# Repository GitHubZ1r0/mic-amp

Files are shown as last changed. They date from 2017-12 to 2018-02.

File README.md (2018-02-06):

# Microphone amplifier for Knowles Electret microphones

## Overview
This printed circuit board (PCB) is based on the design created at Eaton
Peabody Laboratories (Mass. Eye and Ear Infirmary), but redesigned to work at
lower frequencies. It features:

* High-pass input filter with 96 Hz cutoff.
* Selectable 20 or 40 dB gain
* Low-pass amplification with a 72 kHz cutoff.
* Low-noise 1.5V supply for microphone with a low-pass filter cutoff of 0.33 Hz
  (ensuring that very little noise makes it into the microphone).

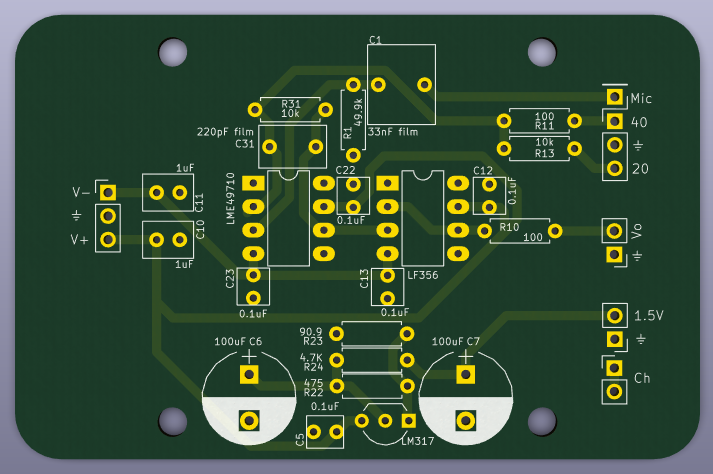
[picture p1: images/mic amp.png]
Rendering of PCB


The board is 74mm x 48mm and the mounting holes, spaced 40mm x 40mm, are sized
for a M3 screw. The board will fit in a Hammond enclosure that accomodates 75mm
wide boards.

## Getting started
OSH Park will print and ship three of these boards for approximately $30. 

Order the parts from the [bill of materials](part%20list.md).

Solder the parts using solder with water-soluble flux.

Wash the board with dH<sub>2</sub>O.

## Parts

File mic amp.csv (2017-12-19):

Reference | Quantity | Value | Footprint | Datasheet
C1 | 1 | 33nF film | Capacitor_THT:C_Rect_L7.2mm_W8.5mm_P5.00mm_FKP2_FKP2_MKS2_MKP2
C10 C11 | 2 | 1uF | custom:C_Rect_L5.5mm_W3.15mm_P2.50mm
C12 C13 C22 C23 | 4 | 0.1uF | custom:C_Rect_L4.5mm_W3.15mm_P2.50mm
C31 | 1 | 220pF film | Capacitor_THT:C_Rect_L7.2mm_W4.5mm_P5.00mm_FKS2_FKP2_MKS2_MKP2
C5 | 1 | 0.1uF | custom:C_Rect_L5.5mm_W3.15mm_P2.50mm
C6 C7 | 2 | 100uF | Capacitor_THT:CP_Radial_D10.0mm_P5.00mm
J2 | 1 | CONN_01X01 | Conn_PinSocket_2.54mm:PinSocket_1x01_P2.54mm_Vertical
J3 | 1 | CONN_01X03 | Conn_PinSocket_2.54mm:PinSocket_1x03_P2.54mm_Vertical
J4 J5 J6 J7 | 4 | CONN_01X01 | MountingHole:MountingHole_3.2mm_M3
J1 J8 | 2 | CONN_01X02 | Conn_PinSocket_2.54mm:PinSocket_1x02_P2.54mm_Vertical
J9 | 1 | CONN_01X05 | Conn_PinSocket_2.54mm:PinSocket_1x05_P2.54mm_Vertical
R1 | 1 | 49.9k | Resistor_THT:R_Axial_DIN0207_L6.3mm_D2.5mm_P7.62mm_Horizontal
R10 R11 | 2 | 100 | Resistor_THT:R_Axial_DIN0207_L6.3mm_D2.5mm_P7.62mm_Horizontal
R13 R31 | 2 | 10k | Resistor_THT:R_Axial_DIN0207_L6.3mm_D2.5mm_P7.62mm_Horizontal
R22 | 1 | 475 | Resistor_THT:R_Axial_DIN0207_L6.3mm_D2.5mm_P7.62mm_Horizontal
R23 | 1 | 90.9 | Resistor_THT:R_Axial_DIN0207_L6.3mm_D2.5mm_P7.62mm_Horizontal
R24 | 1 | 4.7K | Resistor_THT:R_Axial_DIN0207_L6.3mm_D2.5mm_P7.62mm_Horizontal
U1 | 1 | LME49710 | Package_DIP:DIP-8_W7.62mm_LongPads
U2 | 1 | LF356 | Package_DIP:DIP-8_W7.62mm_LongPads
VREG1 | 1 | LM317 | Package_TO_SOT_THT:TO-92_Inline_Wide

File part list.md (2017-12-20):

| References             | Number | Value      | Part number        | Note                                                   |
| ---------------------- | ------ | ---------- | ------------------ | ------------------------------------------------------ |
| C1                     | 1      | 33nF       | FKP2C023301L00HI00 | use metal film                                         |
| C5, C12, C13, C22, C23 | 5      | 0.1uF      | RDER72A104K1S1H03A |                                                        |
| C6, C7                 | 2      | 100uF      | UKL1V101KPDANA     |                                                        |
| C10, C11               | 2      | 1uF        | RDER72A105K2P1H03B |                                                        |
| C31                    | 1      | 220pF      | FKP2D002201D00HSSD | use metal film                                         |
| J1, J8, J10            | 3      | CONN_01X02 |                    | 0.1" header                                            |
| J2                     | 1      | CONN_01X01 |                    | 0.1" header                                            |
| J3, J9                 | 2      | CONN_01X03 |                    | 0.1" header                                            |
| J4, J5, J6, J7         | 4      | CONN_01X01 |                    | mounting hole                                          |
| R1                     | 1      | 49.9k      | YR1B49K9CC         |                                                        |
| R10, R11               | 2      | 100        | YR1B100RCC         |                                                        |
| R13                    | 1      | 1k         | YR1B1K0CC          |                                                        |
| R22                    | 1      | 475        | YR1B499RCC         |                                                        |
| R23                    | 1      | 90.9       | YR1B90R9CC         |                                                        |
| R24                    | 1      | 4.7K       | YR1B4K75CC         |                                                        |
| R31                    | 1      | 10k        | YR1B10KCC          |                                                        |
| U1                     | 1      | LME49710   | LME49710NA/NOPB    | this part is end-of-life, order extra if you need more |
| U2                     | 1      | LF356      | LF356N/NOPB        |                                                        |
| VREG1                  | 1      | LM317      | LM317LZ/NOPB       |                                                        |

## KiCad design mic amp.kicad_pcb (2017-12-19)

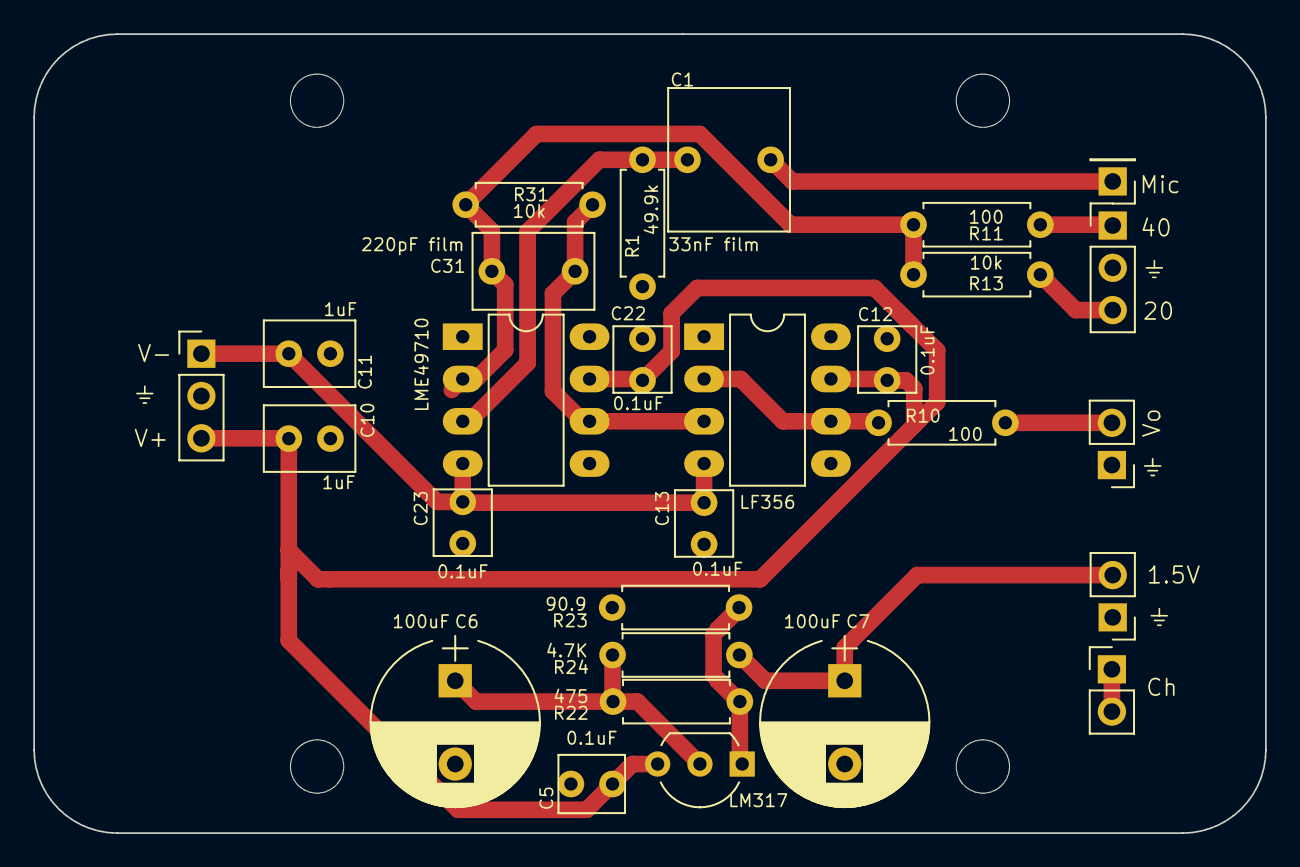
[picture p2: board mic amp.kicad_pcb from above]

Board: 2 copper layers, 74.0 x 48.0 mm, 32 parts (0 on the bottom side), 15 nets.

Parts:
C1: 33nF film; C_Rect_L7.2mm_W8.5mm_P5.00mm_FKP2_FKP2_MKS2_MKP2
C5, C12, C13, C22, C23: 0.1uF; C_Rect_L4.0mm_W3.5mm_P2.50mm
C6, C7: 100uF; CP_Radial_D10.0mm_P5.00mm
C10, C11: 1uF; C_Rect_L5.5mm_W4.0mm_P2.50mm
C31: 220pF film; C_Rect_L7.2mm_W4.5mm_P5.00mm_FKS2_FKP2_MKS2_MKP2
J1, J8, J10: CONN_01X02; PinSocket_1x02_P2.54mm_Vertical
J2: CONN_01X01; PinSocket_1x01_P2.54mm_Vertical
J3, J9: CONN_01X03; PinSocket_1x03_P2.54mm_Vertical
J4, J5, J6, J7: CONN_01X01; MountingHole_3.2mm_M3
R1: 49.9k; R_Axial_DIN0207_L6.3mm_D2.5mm_P7.62mm_Horizontal
R10, R11: 100; R_Axial_DIN0207_L6.3mm_D2.5mm_P7.62mm_Horizontal
R13, R31: 10k; R_Axial_DIN0207_L6.3mm_D2.5mm_P7.62mm_Horizontal
R22: 475; R_Axial_DIN0207_L6.3mm_D2.5mm_P7.62mm_Horizontal
R23: 90.9; R_Axial_DIN0207_L6.3mm_D2.5mm_P7.62mm_Horizontal
R24: 4.7K; R_Axial_DIN0207_L6.3mm_D2.5mm_P7.62mm_Horizontal
U1: LME49710; DIP-8_W7.62mm_LongPads
U2: LF356; DIP-8_W7.62mm_LongPads
VREG1: LM317; TO-92_Inline_Wide

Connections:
+15V: C5.1, C10.1, C12.2, C22.2, J9.3, U1.7, U2.7, VREG1.3
-15V: C11.1, C13.2, C23.2, J9.1, U1.4, U2.4
GNDA: C5.2, C6.2, C7.2, C10.2, C11.2, C12.1, C13.1, C22.1, C23.1, J1.1, J3.2, J8.1, J9.2, R1.1, R23.2
unnamed: C1.1, R1.2, U1.3
unnamed: C1.2, J2.1
unnamed: C6.1, R22.2, R24.1, VREG1.2
unnamed: C7.1, J1.2, R24.2
unnamed: C31.1, R31.2, U1.6, U2.3
unnamed: C31.2, R11.2, R13.2, R31.1, U1.2
unnamed: J3.1, R11.1
unnamed: J3.3, R13.1
unnamed: J8.2, R10.2
unnamed: J10.1, J10.2
unnamed: R10.1, U2.2, U2.6
unnamed: R22.1, R23.1, VREG1.1

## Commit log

2015-11-20 Commit before major revisions
    [mic amp.csv, mic amp.dsn, mic amp.kicad_pcb, mic amp.sch]
2017-11-29 ENH: Updated through-hole version
    [mic amp.kicad_pcb, mic amp.sch]
2017-11-29 Add gerber files and gitignore
    [mic amp-B.Cu.gbr, mic amp-B.Mask.gbr, mic amp-B.Paste.gbr, mic amp-B.SilkS.gbr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]
2017-12-19 Through-hole version of mic amp
    Printed via OSH park. Part list availbale via Mouser (see 171218 mic amp
    project). Designed to fit a Hammond enclosure that accomodates 75mm wide
    PCBs.
    [mic amp-B.Cu.gbl, mic amp-B.Mask.gbs, mic amp-B.SilkS.gbo, mic amp-Edge.Cuts.gm1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]
2017-12-20 Update readme and added parts list and PCB image
    [mic amp.sch]
2017-12-20 Update parts list, fix circuit board image
    [mic amp.sch]
